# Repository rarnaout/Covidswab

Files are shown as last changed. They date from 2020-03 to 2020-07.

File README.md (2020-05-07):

*Last updated: May 7, 2020*

# Manufacturing NP swabs

Large-scale virological testing for SARS-CoV-2, causative agent of COVID-19, has resulted in an acute shortage in NP swabs across the United States. Ad hoc groups from academia and industry have formed to address this crisis. **This repository organizes output from these efforts**.

The purpose is to **update medical professionals and manufacturers**.

Note the location of the repo has changed.

**Several groups have been testing** various materials and geometries using various protocols. Details:

[Beth Israel Deaconess Medical Center (BIDMC) <i>**Udated May 7**</i>](BIDMC/) | [University of Southern Florida (USF)](USF/) | [University of Washington (UW)](UW/) | [Stanford University](Stanford/) | United States Army

For those with in-house 3D printing capacity who are in the direst need, USF has graciously made an <a href="https://usf.box.com/s/wxmlj0r66vp8bzei6o7sur1kq1jr8o1i">STL file available, along with instructions that you should read first</a>. **However, <u>we strongly caution that NP swabs are a serious undertaking that can carry risk to patients if not carefully evaluated, by professionals, at multiple steps of development and use (e.g. design, materials)</u>, as the groups listed here have been doing. If you can work with a known manufacturer, you are strongly encouraged to do so instead of printing your own swabs.**

**All readers** are reminded that swabs are an FDA Class 1 exempt medical device not suitable for "garage testing." ENT, ER, and ID personnel do not need more work removing foreign bodies from/repairing damage to/treating infections in nasal cavities.

At this point **we discourage randomly printing/testing STL files**; instead please see results from testing sites above (esp. [USF](/USF), if you have your own printing capacity).

The content here is **not medical advice.**

Progress has been possible only because of the **extraordinary openness and sharing** of everyone involved, an inspirational and selfless victory over ego and related temptations.

As we move closer to large-scale manufacturing, contracts, etc. participants are asked to **involve their respective communications offices** before using each others' names in any promotional materials.

We are driven by a **single, common goal: stopping this pandemic.**

Anything is this repo is provided **[freely and openly](Participant_Agreement/)** in the spirit of cooperation for the free use for all.

### Disclaimer

The information and designs in this repository are being made available for research and informational purposes only.  The products described in this repository may be regulated as medical devices depending on their intended use.  The information and designs are made available without any representations or warranties of any kind, including that the designs do not infringe any third-party rights or are appropriate for use in the manufacturing of medical devices.  Any product feedback offered by any medical professional or employee of a hospital provided through this repository does not constitute medical advice or an endorsement of any particular design. Any use of the information or designs in this repository is at the sole risk of the user.

## Contact

BIDMC: Ramy Arnaout, MD, DPhil rarnaout at-sign bidmc dot harvard dot edu 617-538-5681

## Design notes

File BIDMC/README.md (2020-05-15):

*Last modified: Thursday, May 7, 2020*

# Results summary, BIDMC

## Wednesday, May 13, 2020

Our work, detailing NP swab development and clinical validation, has now been peer reviewed and published by the <a href="https://jcm.asm.org/content/early/2020/05/11/JCM.00876-20"> Journal of Clinical Microbiology</a>.

Clinically validated swabs are now available to <a href="https://printedswabs.org/"> order</a>

## Thursday, May 7, 2020

The <a href="https://www.medrxiv.org/content/10.1101/2020.04.14.20065094v2">second version</a> of our preprint is now up on medRxiv, including results from HP, Inc (Abiogenix/Fathom).

## Monday, May 4, 2020

**Regarding viral transport media,** colleagues here at BIDMC have posted a preprint describing the <a href="https://www.medrxiv.org/content/10.1101/2020.04.29.20085514v1">large-scale, in-house production of viral transport media to support SARS-CoV-2 PCR testing in a multi-hospital healthcare network during the COVID-19 pandemic</a>. If you need to produce your own media, please see this manuscript.

## Sunday, April 19, 2020--updated Friday, April 24, 2020

<a href="https://www.medrxiv.org/content/10.1101/2020.04.14.20065094v1">The first results of our field trial are now on medRxiv</a>. (Note apparently medRxiv has been having issues.) In addition to what's in the preprint, a prototype from HP, Inc. has also passed our trial. We will be updating medRxiv as we can.

The participant information sheet we used is <a href="BIDMC_participant_information_sheet.pdf">here</a>. **Remember, approval of such a document requires approval of Your IRB.**

The raw data for Fig. 2 is <a href="fig2_data.txt">here</a>.

Contact information for manufacturers is <a href="https://printedswabs.org">here</a>.

**We continue to make our work freely available to help everyone address the crisis. If you use any of the work here, please do cite the repo and the prprint, Callahan et al. medRxiv 2020.**

## Friday, April 17, 2020

**A brief note: we have received very many requests for our results regarding FormLabs' prototypes. You can find them in <a href="np_swab_results.xlsx">this Excel spreadsheet</a>. None of the prototypes we received from FormLabs passed our Phase I testing. We deemed them too brittle. Therefore none entered our clinical trial. If you have questions about clinical evaluation of FormLabs' swabs, please contact USF/Northwell, as they are the ones with the most experience with these swabs in a clinical context and can advise.**

## Wednesday, April 15, 2020

This entry contains a short summary of progress over the past 10 days at BIDMC, one of the many groups that are working together to resolve the NP swab shortage. It will also try to address frequently-asked questions.

### Contents
- <a href="#field_trial">Field trial results</a>
- <a href="#irb">BIDMC IRB materials for reuse</a>
- <a href="#process_041520">Process update</a>

### Field trial results

About two weeks ago we began an IRB-approved field trial of select prototypes that had passed our initial phases of testing. (Please see prior updates for details of those phases.)

The main goal of the trial was to measure concordance between each prototype and a control, for which we used Copan model 501CS01, one of the FDA's approved standard (flocked) NP swabs. Participants were drawn from the pool of people clinically suspected of COVID-19 who were given appointments at BIDMC's drive-through testing facility.

Specifically, the goal was to collect a prototype as well as a control NP swab on each participant until we had 10 SARS-CoV-2-positive and SARS-CoV-2-negative controls. These were all tested on our in-house Abbott m2000s.

To date prototypes from three manufacturers have completed the trial, with others at various stages. The three are from Resolution Medical (crafted with Carbon3D technology), EnvisionTec, and Origin.io. (Note we have not tested FormLabs.) These all exhibited a high degree of concordance with the controls. Analysis of Ct values showed no statistical evidence of bias, although the numbers are small. Participants tolerated the prototypes to varying degrees.

We have written up the results and posted them to medRxiv so everyone can see details; unfortunately it is taking a bit longer to get a link from them than we wished but we will post it here.

Manufacturers are continuing to iterate on their designs.

The trial is ongoing.

### BIDMC IRB materials for reuse

To help others who want to run a trial, we have made <a href="BIDMC_IRB_key_info.pdf">relevant sections from our IRB available</a>, including <a href="BIDMC_participant_information_sheet.pdf">participant information sheet</a>. If you use them, please cite Callahan et al., medRxiv 2020 (link pending).

### Process update

Manufacturers have launched a <a href="https://printedswabs.org/">site for connecting hospitals with manufacturers</a>. To our knowledge, not all manufacturers appear there. Appearing on that site does not count as an endorsement from BIDMC.

We continue to receive many inquiries. If you are a manufacturer interested in our testing your swabs, the best thing is to send a high-resolution image and, if you can (to cut down on lead time, but unfortunately not as a guarantee we will test), send a complete description (including manufacturer; sender; manufacturing technique; detailed measurements of head, neck, breakpoint, and shaft; production volume now, in one week, and in one month), to CLS624 c/o Cody Callahan, 3 Blackfan Circle, Boston, MA 02215.

Regarding phone and email inquiries: we are happy to help as we can but please do read all the information here and below before sending an email or placing a call, as  your questions may already be answered.

## Friday, April 3, 2020

This entry contains a summary of progress over the past week at BIDMC, one of the many groups that are working together to resolve the NP swab shortage. It will also try to address frequently-asked questions.

### Contents
- <a href="#phase1">Phase I testing: expert evaluation, collection sufficiency, PCR compatibility</a>
- <a href="#phase2">Phase II testing: decontamination, packaging, volume</a>
- <a href="#phase3">Phase III testing: field trial (IRB)</a>
- <a href="#self">Self-printing</a>
- <a href="#process">Process update</a>
- <a href="#next">Next steps</a>

### Phase I testing: expert evaluation, collection sufficiency, PCR compatibility

Earlier this week we completed <a href="../BIDMC/np_swab_results.xlsx">Phase I testing</a> of over 140 materials and prototypes from approximately two dozen manufacturers and other groups.

This phase consists of three steps: (i) expert evaluation, (ii) collection sufficiency (using Gram stain of cheek swab as a proxy for the nasopharynx), (iii) compatibility with our Covid-19 PCR test (we are currently using the Abbott system).

At this point we have completed many (>5-10) iterations of prototypes with several manufacturers, at each step offering design feedback and guidance, working with their engineers, and they have been unbelievably responsive and ingenious in working with us.

### Phase II testing: decontamination, packaging, volume

As we have moved past Phase I, we considered the ability to decontaminate, with a preference for autoclaving; the ability to package singly, and to produce swabs at high volume---hundreds of thousands of units per day or more---and for low cost. This evaluation was done again through many interations with manufacturers.

These two phases resulted in our selection of four prototypes at present---from Carbon3D, EnvisionTEC, Hewlett Packard, and Origin 3D Manufacturing---for Phase III testing, a field trial under IRB (below).

#### How to interpret our selections

We have chosen the prototypes that, per our Phase I and II evaluation above, performed best.

We have chosen prototypes produced via different technologies and materials to maximize our probability of finding solutions and minimize the probability that unforeseen issues results in a future supply bottleneck (such as the one that led to this crisis). We are fortunate that our Covid and respiratory pathogen testing bandwidth at BIDMC allows for testing at scale.

The prototypes we have chosen reflect our best judgment. The Phase I data is collected and freely available to others in this directory. We recognize that others are free to reach their own conclusions and that specific requirements may differ by setting.

#### Additional prototypes

We announced that we would be testing everything received before 5 p.m. Eastern this past Monday, March 2. Mainly for bandwidth reasons we are discouraging new submissions at BIDMC. Other sites may still be accepting. We will try to facilitate connecting manufacturers with additional testing sites if we are asked.

### Phase III testing: field trial (IRB)

As mentioned above, today we began field testing under an IRB. Briefly we are collecting 10 positives and 10 negatives for control swabs and each prototype and testing concordance. We will make details available in this folder as soon as we can. We may add additional prototypes in the future. We will report results in collaboration with the manufacturers.

### Self-printing

We have received many inquiries regarding self-printing. We understand there are sites with on-site 3D printing capacity but effectively no swabs for whom this is a particularly urgent issue. While **we strongly encourage waiting to purchase from a manufacturer if at all possible**, we point those in this urgent situation to the work of Dr. Summer Decker at USF and of FormLabs, who have <a href="https://usf.box.com/s/wxmlj0r66vp8bzei6o7sur1kq1jr8o1i">made available an STL file and a readme</a>. This statement should not be read as an endorsement: the FormLabs solution was not selected for Phase III testing at BIDMC. Our Phase I evaluation of the material for this solution, as for all others we tested, is in the Excel spreadsheet. Again, others are free to reach their own conclusions. **Please read the  disclaimers on this repo's main page, and USF's readme, carefully.**

### Process update

As we move toward what we anticipate will be a successful resolution to this crisis, we understand that competition for credit and contracts will intensify. This is natural. However, **we believe the fastest solution is to remain as collaborative as possible. We encourage manufacturers, and also testing sites, to share as much as they can**. This includes materials testing, protocols, IRBs, and results.

We can give you a folder and write access to post to the repo, for those who want but do not have it. Meanwhile, please make clear what you do not want shared.

### Next steps

We anticipate results of our field trial soon, which we hope to share here and on a 5-minute call.

## Friday, March 27, 2020

This entry contains results of testing over the past two days, as manufacturers have iterated their materials and designs, specifically to **combine** tip and shaft geometries that we preferred with preferred materials.

Please see Wednesday's entry (below) for context.

### Contents
- <a href = "#done">What we have done and not done</a>
- <a href = "#trial">Clinical trial</a>
- <a href = "#decon">Decontamination/sterilization</a>
- <a href = "#package">Packaging</a>
- <a href = "#schedule">Our testing schedule</a>
- <a href = "#guidance">Guidance to other institutions</a>
- <a href = "#notable">Notable performers</a>

### What we have done and not done

In total we have tested <a href="np_swab_results.xlsx">over 100 materials and geometries</a>, contributed by over a dozen groups and individuals.

Prototypes mentioned below pass all three of our initial evaluations: <a href="../BIDMC/Methodology.pdf">design evaluation</a>, <a href="../BIDMC/Methodology.pdf">collection sufficiency</a>, and <a href="../BIDMC/Methodology.pdf">PCR compatibility</a>. **This testing does not constitute a clinical trial.**

### Clinical trial

**None of the prototypes we have received been field tested** yet at BIDMC. An IRB/trial are in preparation (ceding to USF's WIRB). It is not currently our plan at BIDMC to recommend any swab without such trial.

The below does **not** include evaluation of prototypes received after Thursday afternoon; we are working on those now.

**Note for those with in-house 3D printers:** [USF](/USF) has begun field testing of their self-printed swabs.

### Decontamination/sterilization

There is not yet **consensus on sufficient decontamination/sterilization** techniques. Three options are:

- Preferred: autoclaving packaged product
- Backup: ethanol/isopropanol decontamination
- Unknown: vapor-peroxide sterilization

We ask manufacturers of favored designs to tell us what materials are **known to tolerate** these methods, and whether they can be done before delivery.

### Packaging

Single-swab packaging is preferred.

Discussions on these are ongoing. See also note below.

### Our testing schedule

We will continue to evaluate new swabs **received before 5 p.m. ET on Monday, March 30.**

### Guidance to other institutions

**If you can wait** for results of field-testing trials for the above, which gate large-scale production, we recommend you do so.

**If you cannot wait** and have in-house 3D printing capacity, we recommend you [read the University of South Florida's results](/USF), since they have field-tested in-house printed solutions (I believe from FormLabs).

### Notable performers, all-in-one

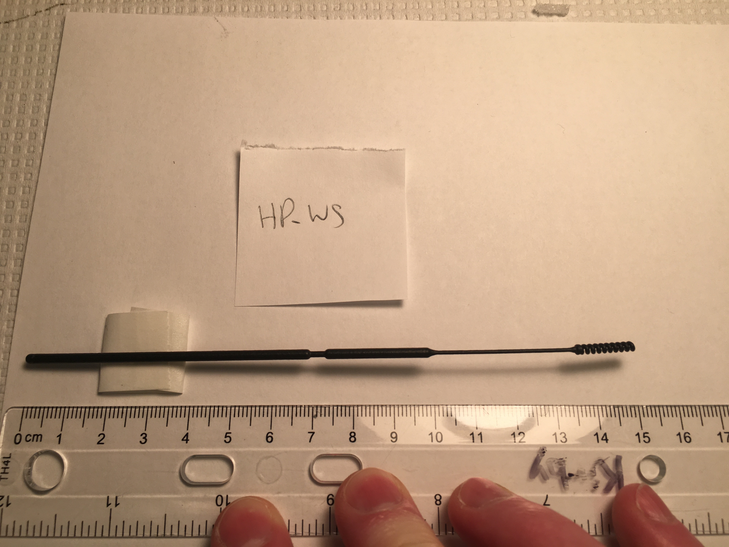
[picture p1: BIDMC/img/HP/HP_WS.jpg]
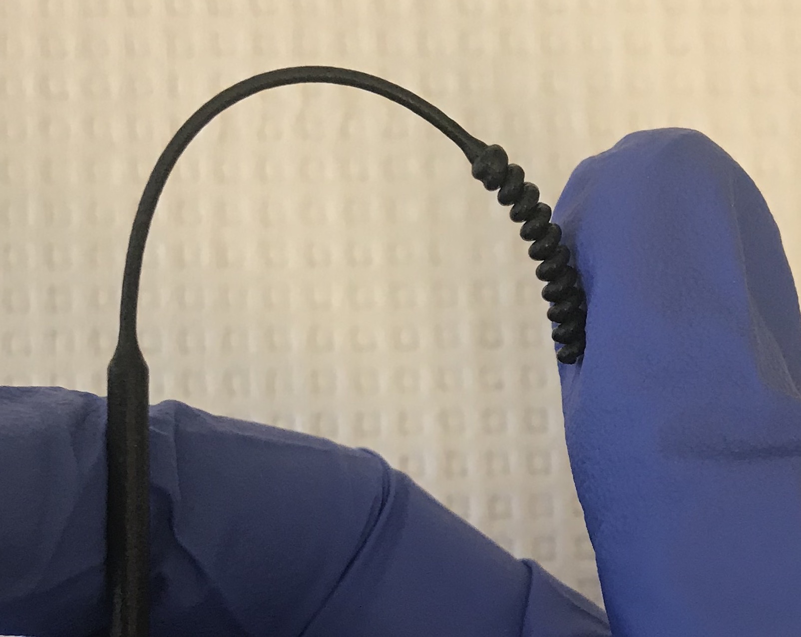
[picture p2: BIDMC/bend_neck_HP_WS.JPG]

HP "WS"

The notability here is the material, which has the same stiffness bendability as the previous version but has a smooth finish. It is autoclavable. The shaft is the preferred design. The breakpoint is a bit difficult to break but acceptable. The tip shown is acceptable but not preferred.

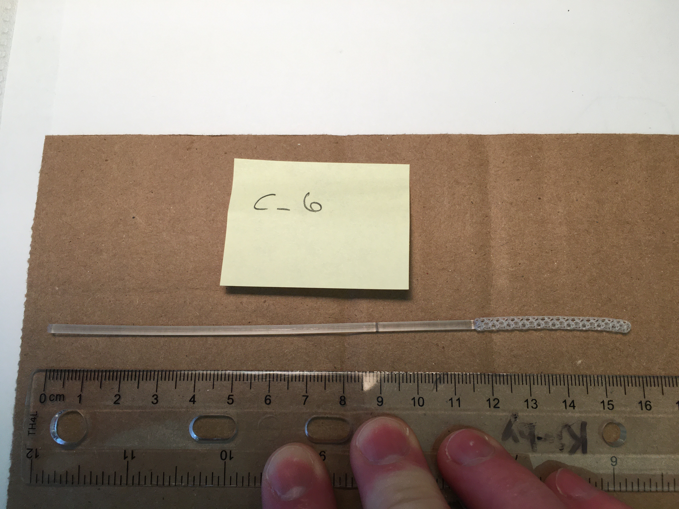
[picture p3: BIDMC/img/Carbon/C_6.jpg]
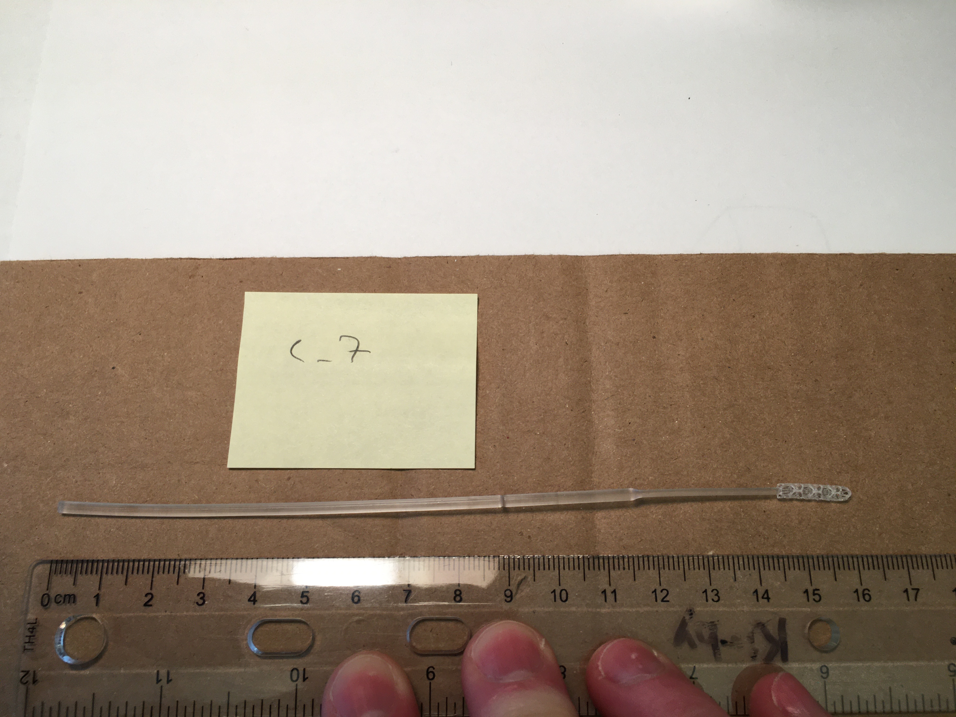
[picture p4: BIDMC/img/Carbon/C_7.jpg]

Carbon "C-6" (left) and Carbon "C-7"

The empty structure collects sufficient specimen. The central spine of the tip provides sufficient rigidity and flexibility. The longer tip provides similar or greater flexibility than the thin neck. The material is not autoclavable but does tolerate alcohol disinfection.

We reiterate that we consider many <a href="#tip">tip designs</a> as passable.

### Contact

Please contact jennifer.kritz@bilh.org for press inquiries.

Please contact Dr. Ramy Arnaout, MD, DPhil rarnaout@bidmc.harvard.edu for technical/clinical issues, and Cody Callahan ccallah4@bidmc.harvard.edu for everything else (including coordinating deliveries/testing).

## Wednesday, March 25, 2020

This document summarizes BIDMC's evaluation of dozens of [**geometries**](#geometries) (swab designs) and [**materials**](#materials) ([full data here](np_swab_results.xlsx)), with brief comments on [**decontamination/sterilization** and **packaging**](#decon), [**production volume**](#volume), and [**clinical trials**](#trials).

- <a href = "#geometries">Geometries</a>
- <a href = "#materials">Materials</a>
- <a href = "#decon">Decontamination/sterilization and packaging</a>
- <a href = "#volume">Production volume</a>
- <a href = "#trials">Clinical trials</a>
- <a href = "#contact">Contact</a>

## Geometries

**Note:** examples shown are not necessarily the preferred material and not necessarily from the manufacturer who created the design. No attribution of credit is made or implied by this listing.

### Tip

Tip should:

- collect sufficient material (see Gram stains below)
- not end in a sharp tip (e.g., spring geometry ends in sharp tip; if tip is connected to support regardless of geometry, result is a sharp tip)
- maximize surface area
- be flexible (more flexible than bic pen)
- restore elastically to straight (even after multiple bending)

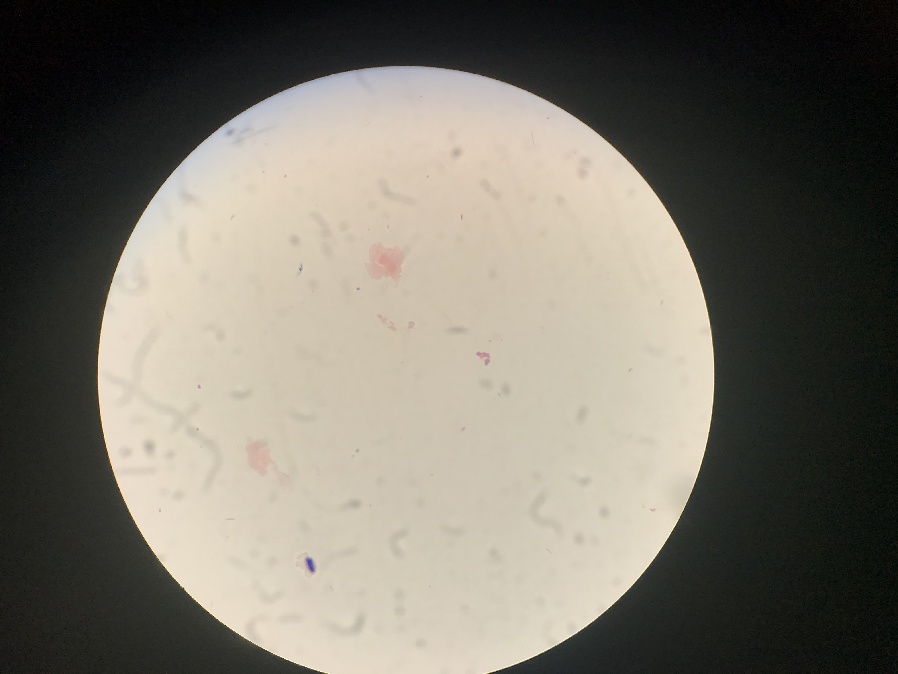
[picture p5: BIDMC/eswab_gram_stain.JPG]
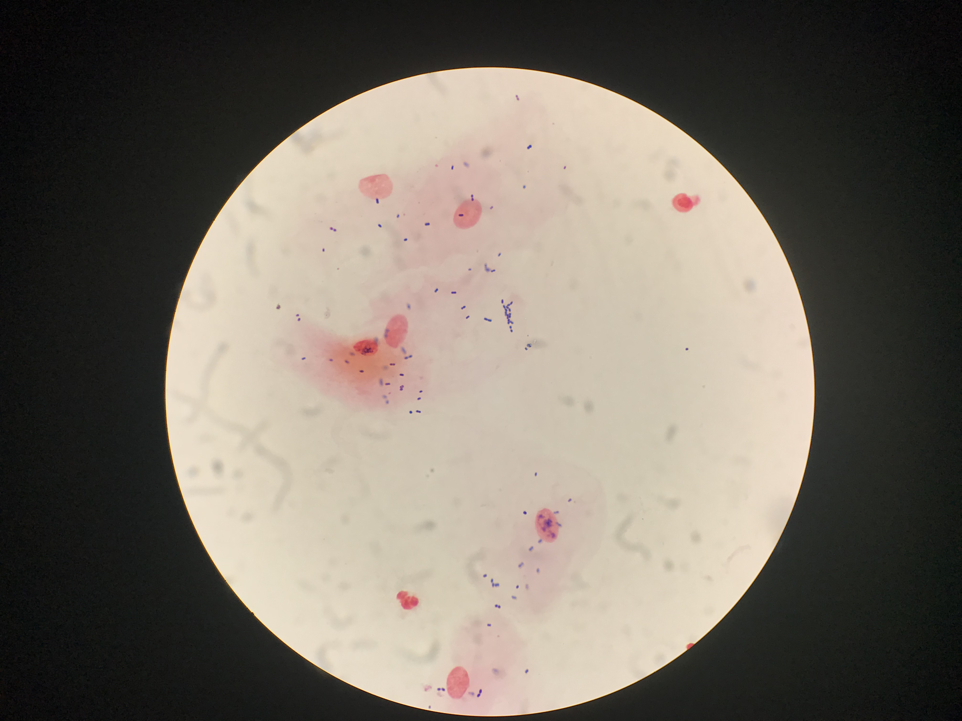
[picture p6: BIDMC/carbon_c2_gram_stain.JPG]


Reference (left) and passing-quality (right) Gram stains of cheek swabs. Epithelial cells (large faint pink) and (Gram-positive) bacteria (small purple) are clearly seen. Many Gram stains of the prototype NP swabs under evaluation (like the one at right) collected more material than the reference (left), but this should not be interpreted quantitatively (a lot/a little), only qualitatively (yes/no).

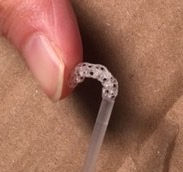
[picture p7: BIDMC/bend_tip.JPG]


Tip flexibility

#### Preferred tip:

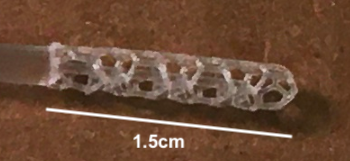
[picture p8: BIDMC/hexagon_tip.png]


Hexagon (Carbon3D)

This was preferred because the hollowness captured a lot of material, while also being reasonably stiff. This was not a strong preference.

#### Also acceptable (no order):

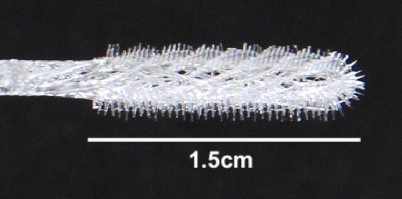
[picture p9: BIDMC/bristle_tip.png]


Bristle (OPT)

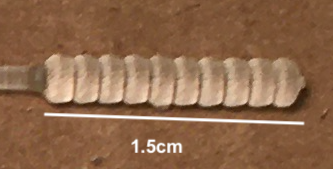
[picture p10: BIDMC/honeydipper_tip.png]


Honeydipper (FormLabs)

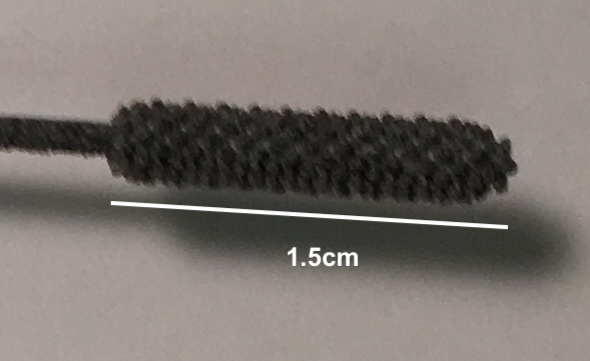
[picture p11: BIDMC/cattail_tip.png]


Cattail (HP print of ?USF design)

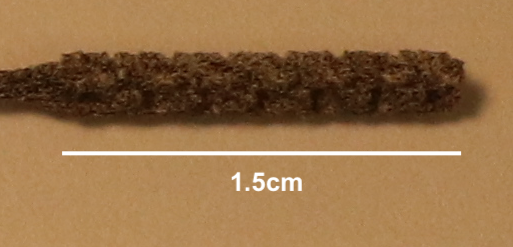
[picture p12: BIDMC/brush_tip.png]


Brush (HP print of ?USF design)

Note none of these are [flocked]("https://github.com/HMS-RIC/Covid19-NP-Swab/#flock"). FDA says flock is **preferred** but **not required**.

### Shaft

#### Preferred shaft:

3mm-diameter tip, 1mm-diameter neck, 2.5mm-dimater handle and \~2mm breakpoint located 7cm from tip-end of swab.

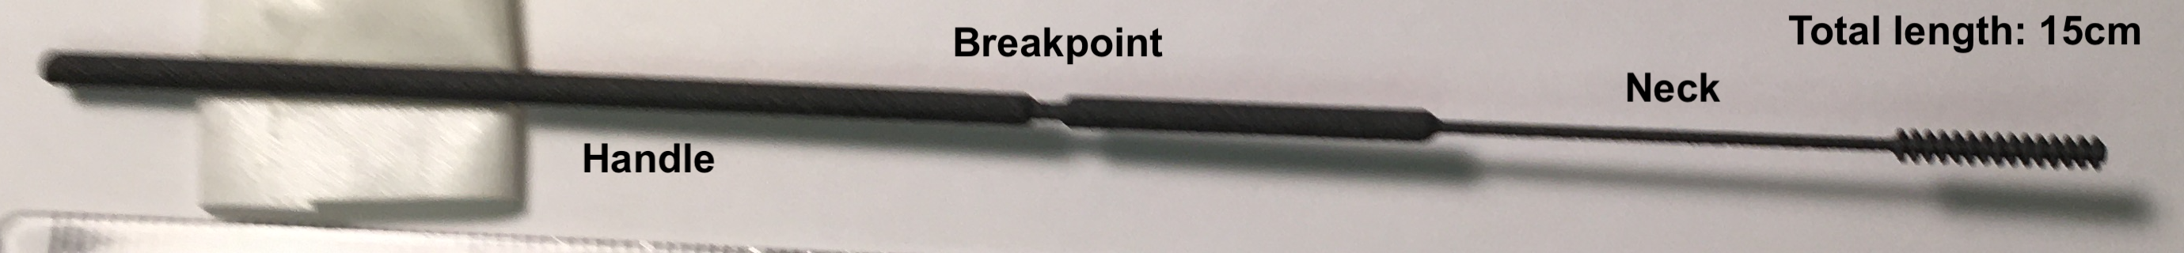
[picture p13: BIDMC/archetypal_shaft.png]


Archetypal (Abiogenix design (?), HP print)

### STL files

We do not have all stl files for all designs tested; what we have are [here](/Covidswab/design_files/). If you need one we don't have, please contact its [creator]("np_swab_results.xlsx"). If you have an stl file to share, please email it to ccallah4@bidmc.harvard.edu with *STL-FILE_\<identifier>_\<company>* in the subject field.

## Materials

### Handling

Key features (best performers in parentheses):

- straight (HP > Carbon3D, FormLabs)
- smooth to the touch (Carbon3D > FormLabs, HP)
- dry (not sticky) (Carbon3D, HP, FormLabs)
- shaft: stiffness comparable to that of the inkholder of a bic pen
- neck and tip: flexible (capable of being bent 180 degrees without breaking, except at the breakopint) (HP, Carbon3D)
- breaks at breakpoint (should be somewhat difficult to do) (HP, FormLabs)
- no dust or other byproduct of printing process

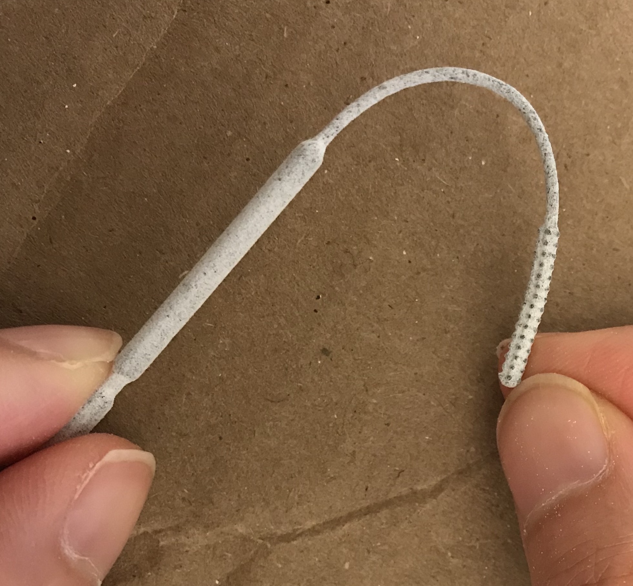
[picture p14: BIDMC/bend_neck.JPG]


Neck flexibility

#### Preferred material:

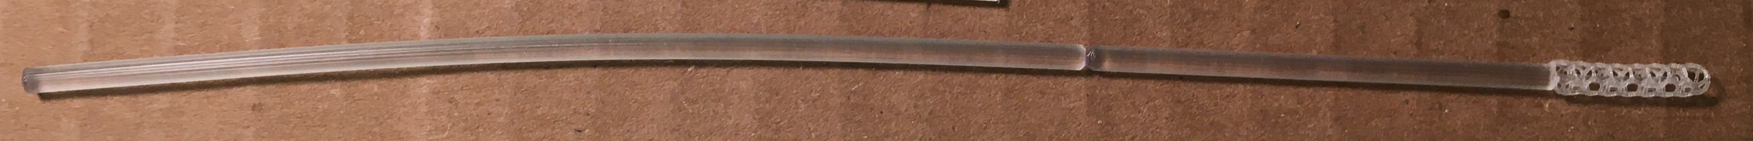
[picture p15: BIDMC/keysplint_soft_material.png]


Keysplint Soft (Carbon3D)

### PCR compatibility

All materials tested so far (as of March 25, 2020) are PCR compatibile (see Excel for any codenames).

**Passed:** OPT, HP ("USF-1"), EnvisionTec (Nilson), FormLabs, Carbon3D, Pavel.

**Pending:** J_1 (Jifei), USF-2, B_1, S_1 (Seriano), EV.

**Not tested (failed clinical testing):** FT

**Not listed here:** materials from compound manufacturing (shaft plus glue plut flock/PDMS)

## Decontamination/sterilization and packaging

Autoclaving preferable, isopropanol or 70% ethanol washes with clean packaging acceptable.

Likely process: swabs produced and washed at scale, then:

- (option 1) take to a company with autoclavable paper packaging (e.g. Georgia-Pacific, 3M), or

- (option 2) packaged at manufacturer's site (e.g. EnvisionTec)

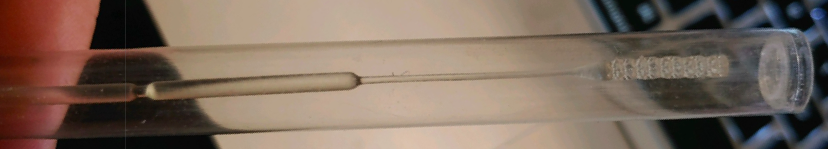
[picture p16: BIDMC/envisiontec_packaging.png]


EnvisionTec's packaging

## Production volume

To my knowledge EnvisionTec, HP, FormLabs, and Carbon3D all have capacity for producing at least hundreds of thousands per day.

## Field testing, safety, market

**Field testing.** Field testing means using swabs on nasopharynx of people with confirmed SARS-CoV-2.

At BIDMC we have tested for appropriateness by (infectious disease/clinical pathologist) expert evaluation, and tested for sufficiency of collection using cheek swab and Gram stain as a surrogate for viral particle collection from nasopharynx. We have **not** field tested.

Field testing requires IRB approval.

To my knowledge Dr. Summer Decker at USF has field-tested at least on non COVID-19-suspected cases. She has an IRB.

I suggest as a first step other clinical sites model after USF's IRB and have their local IRBs cede review to USF as URB of record.

**Safety.** Note swabs are FDA Class-1 exempt devices; "garage testing" not advised.

**Market.** Several tip/shaft/material combinations will likely yield usable products. There will be a competitive market. A/B testing, marketing, contracting, etc. are beyond the scope of this document.

## Injection molding:
For those looking to have injection molded swabs evaluated we encourage you to look through the results of our assessments. <a href="/BIDMC/np_swab_results.xlsx">Here</a>, we offer design feedback and the results of PCR compatibility. In general, effective tip designs have high surface area and are designed not to be abrasive for patients. For material choice, swab rigidness should be comparable to the plastic inkwell of a pen.

In addition, for those looking to reach out, please include information on your ramp up time and daily unit production.

## Contact

Ramy Arnaout, MD, DPhil rarnaout at-sign bidmc dot harvard dot edu 617-538-5681 on behalf of the BIDMC team (not everyone is pictured):

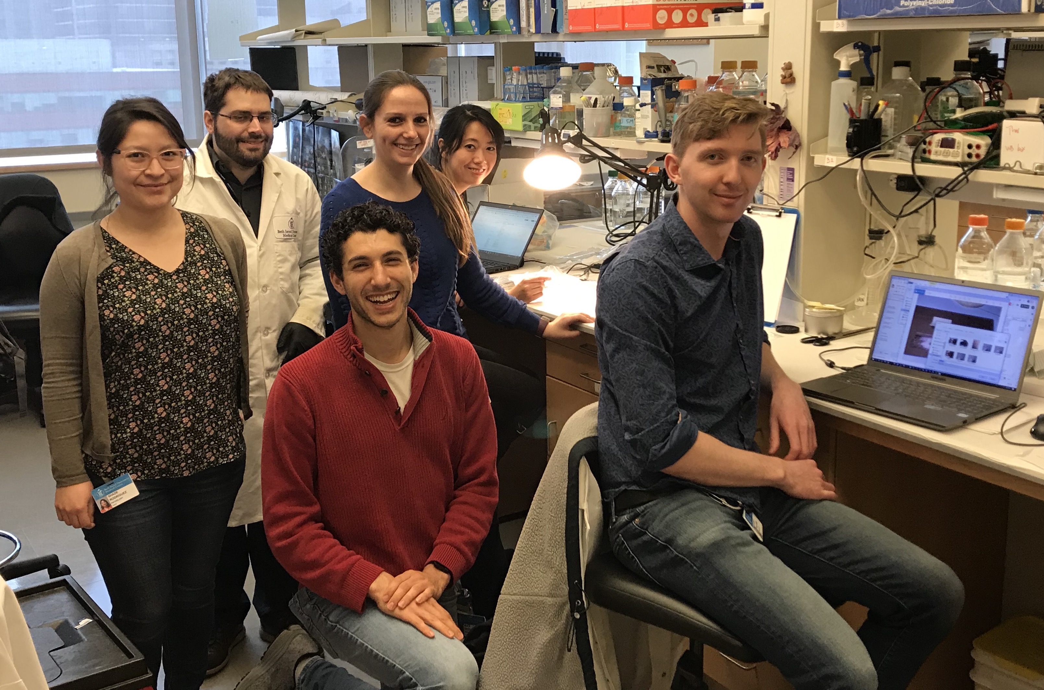
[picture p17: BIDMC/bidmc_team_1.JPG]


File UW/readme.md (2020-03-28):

Notes on work being done in Seattle:

Clinical evaluations were done by Dr. Ellen Lackermann at Pacific Medical Center, she's been working at Pac-Med's drive-through swab clinic.

Sample collection testing was done by Jenny Hu, stains were done on slides with methylene blue instead of gram stain.

PCR compatibility testing done at UW Department of Laboratory Medicine, Virology Division by Keith Jerome's group (using Covid-19 sample)

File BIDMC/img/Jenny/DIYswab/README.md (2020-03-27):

*Last updated: March 23, 2020 00:15 PT*

# VWR 1ul inoculating loop with a strip of Pellon P45 fabrif double knotted through the loop.  

Use a dental floss threader to pull the fabric through loop.  Need to hold the loop while pulling through so it doesn't bend/snap.

video of process here: https://www.dropbox.com/s/hvpb7n1sn2xzr8p/loop%2Bpellon%20p45.mp4?dl=0

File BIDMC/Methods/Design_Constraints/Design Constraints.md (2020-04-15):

# Mechanical Constraints
Swab
- outer diameter of swab is 3mm or less
- minimum swab length is 15cm - *confirm this*
- swab should flex (75 degrees with ?lb load) - *confirm this*
- swab should break 7cm from tip

Swab Bristles
- should be 1.5cm in length
- bristles should maximize surface area
- bristles should not dislodge/break off in body
- bristle head should not break off in body

Swab Break
- part should break first at swab break

# 3D Printing Constraints
Resolution
- minimum feature size/resolution of MJF 3D printing is 0.7mm
Material
- material is PA11 or PA12 nylon - confirmed FDA biocompatible 

# Material Constraints
PCR/Assay Compatability

## Safe: 

- PC, 
- PVC, 
- PP, 
- PTFE, 
- wax with melting point ≥80°C, 
- SiO2 quartz, 
- Pyrex glass, 
- soda-lime glass, 
- NOA68, 
- mineral oil

## Unsafe: 

- PMMA, (incompatible with PCR)
- wax with melting point <80°C, (incompatible with PCR)
- silicon, (incompatible with PCR)
- SO2 5600Å, (incompatible with PCR)
- ITP glass, (incompatible with PCR)
- SU-8, (incompatible with PCR)
- NOA61, (incompatible with PCR)
- epoly glue, (incompatible with PCR)
- acrylic glue (incompatible with PCR)

## Source:

Kodzius et al [paper](kodzius2012.pdf): Inhibitory effect of common microfluidic materials on PCR outcome

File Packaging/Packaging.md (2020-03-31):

# Packaging Prototype Overview

The following is a brief overview of the different packaging methodologies submitted for evaluation. Here, we describe the advantages of each system, as conveyed to us the respective manufacturer and or designer.
<br>
<br>
<br>

## EnvisionTec
<p>
EnvisionTec has an FDA approved single-swab packaging system, that is capable of printing both the swab and container simultaneously.
</p>
<br>

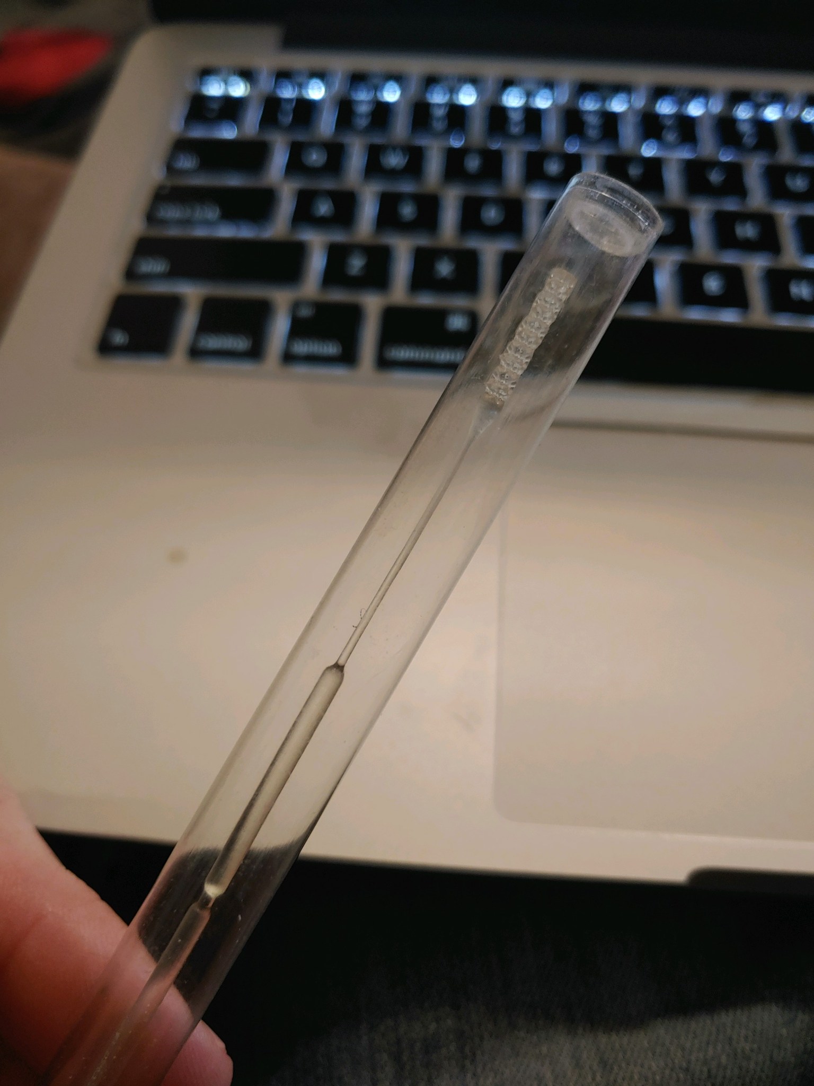
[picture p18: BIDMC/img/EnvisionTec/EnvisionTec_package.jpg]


<br>
<br>
<br>

## Opt Industries
<p>
Opt Industries has provided designs for a multi-swab system to maximize the amount of swabs available per print. In this design, multiple swabs are printed per case, with individual swabs being pulled out of the case as needed.
</p>



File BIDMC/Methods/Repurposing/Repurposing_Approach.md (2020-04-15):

*Last updated: March 20, 2020; info-dumped, needs better organization*

### Scrounging, Repurposing

First a word about scrounging and repurposing. There are lots of swabs used for various things floating around hospitals, outpatient clinics, private practices, and so on. **Be creative and ask everyone you know. That's what we've been doing and it's gotten us thousands of swabs.** This is a stopgap at best, but every swab counts.

Will a repurposed swab work? Find someone who uses NP swabs, take pictures of what you find, and ask that person to weigh in on suitability. (We've been asking our respiratory care personnel.) In practice, as long as the materials are not wood or cotton, there's a chance you've got something usable. **If you find something that works, please tell us,** along with how you know it works, and we'll post it.

There are several alternatives being tried:

- We are looking into using small urine loops as shafts; we don't yet have a solution for how to apply a swab end. Will post if we do. At least there are usually very many of these around in clinical microbiology laboratories
- Printing a bristled head is a no-go for conventional 3D printers, as the features are too small. It is possible that a sand-blasted/chemically etched/otherwise roughened bulb *might* work, but we are not doing research here: we're looking for our best bet for a sure thing
- Mascara brushes. The consensus so far is, the materials might be right but the brushes are far too large/widely spaced. Again, they *might* work, but see above

SWAB-LIKE PRODUCTS
----------------------------------
1) optics (cleaning supplies)
2) cosmetic swabs / applicators
<!-- 3) all the research Ofer and Pavel have done -->

SHAFTS
------------
1) loops (see picture)
2) plastic rod
   1) 2mm nylon fishing line
       comes on a roll but may be stiff enough
   2) plastic rod
3) thin pipettes (Rima)



BRISTLE W/O ADHESIVES
--------------------------------------
1) knurling process to crush plastic to give it a high-surface area feature (can be done with a vice and rough surface plates;  burnish sharp edges)
2) sanding / sand blasting to roughen edges
3) chemical etching to roughen edges
4) reheating plastic locally and forcing into a mold (need to watch out for brittleness)
5) molding/3D printing shape

BRISTLE W/ ADHESIVES
-----------------------------------
1) flocking
2) absorptive foam  (open-cell, like paint-brush)
3) tooth-brush material
4) nylon wool fiber (https://www.polysciences.com/skin/frontend/default/polysciences/pdf/Nylon%20Wool.pdf)
5) panty-hose material (nylon mesh; can be cut and wrapped/wound)
6) synthetic steel wool (https://www.amazon.com/3M-10119NA-Synthetic-Steel-Wool/dp/B00004Z4AE)

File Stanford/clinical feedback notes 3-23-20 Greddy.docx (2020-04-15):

Clinical Feedback meeting notes by Goutam Reddy (greddy@abiogenix.com)

3/23/20 meeting @ Stanford Health

Interviewed: Dr. Linda Barman, Thanh Khong PAC (they run the drive-through swabbings)

Summary of Design Notes:

1) Features too sharp => need a smoother edge (like flocking) - suggested a “rounded Archimedes screw”
2) Need a rounder tip (like bulb of flocked head) w/ “cupping”
3) Need to stiffen break-point and move back
4) Need plastic to bend but not deform => spring back after bending (liked thicker diameter neck models than thinner)
5) Most liked designs #3, #10, #1
6) Finer features not showing up in PA12 prints (PA11 vs PA12?)

Swab Note:

They use a swab with a longer cut-off point. She said our cut-off point was too short (nasal swab vs. nasopharyngeal swab?) Measurements of the swabs they use below:

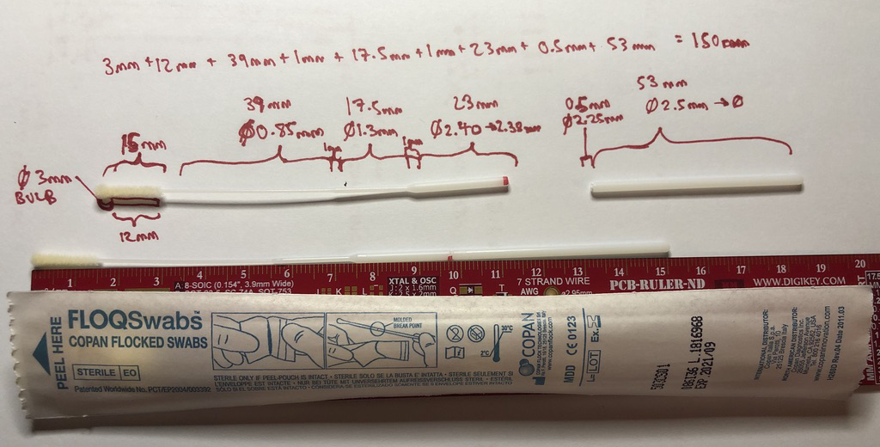
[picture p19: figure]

General Notes:

1) We should test temperature changes of our swabs as they can be sitting in freezing temperatures for drive-through clinics.
2) Asked about sterilization and packaging -> is it autoclavable?
3) Nasopharyngeal space is extremely sensitive (to bleeding, irritation etc…), especially in patients coming in to be swabbed. Err on the side of doing no harm (i.e. swabbing is not a life-saving intervention => we’ll be doing millions of swabs => err on side of gentle np swab and no damage to tissues (no poking, soft interface, no breaking off inside so ENT has to extract)

Test 1) Abiogenix Nubs w/ Holes in PA11 (mfg by HP in San Diego)

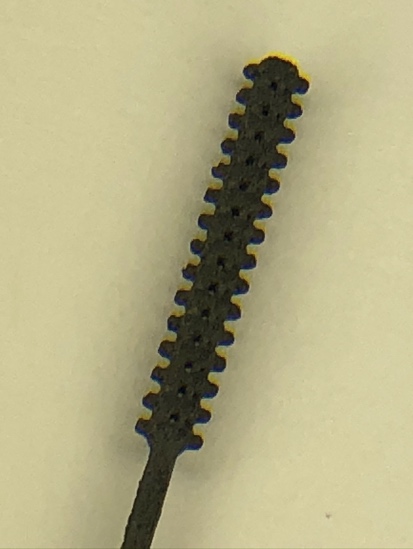
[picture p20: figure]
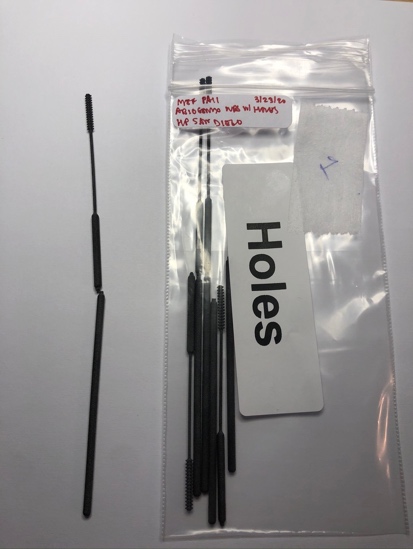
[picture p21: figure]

- too flimsy @ breakoff point => stiffen @ breakoff
- breakpoint too far down
- too rough

Test 2) Abiogenix Nubs w/o Holes in PA11 (mfg by HP in San Diego)

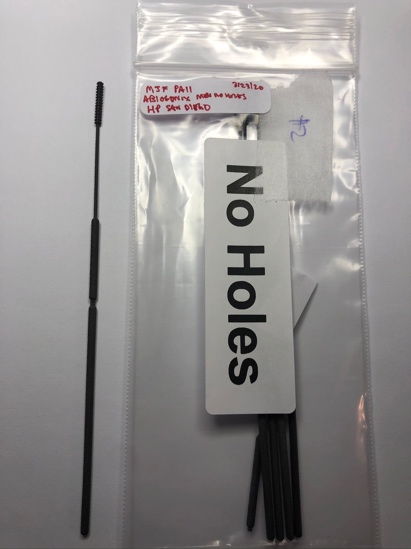
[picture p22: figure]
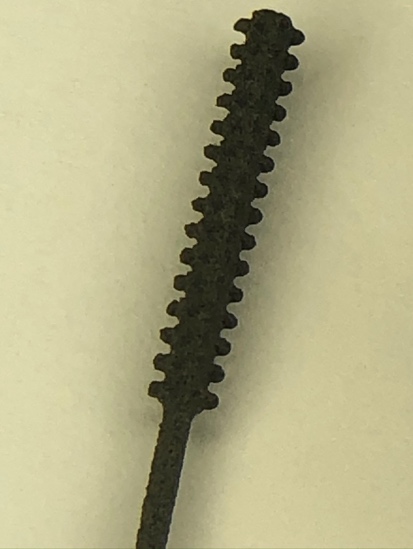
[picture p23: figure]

- needs rounded tip like the bulb on the flocked swab
- tip is too tiny: needs absorption
- passage to nasopharynx has bends, so swab needs to bend but needs to spring back

Test 3) Fathom ??? in PA12 (mfg by Fathom in Oakland)

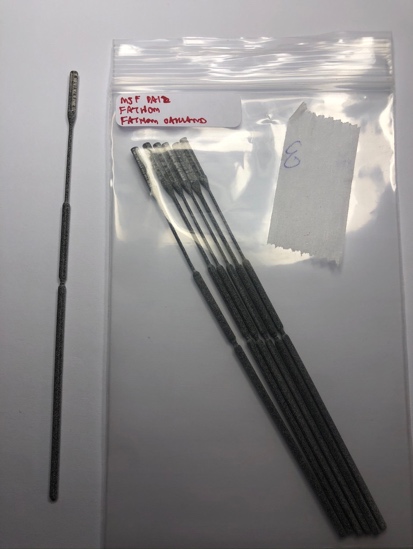
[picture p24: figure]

- liked round tip
- smooth out
- make neck longer
- good size
- good front
- good neck

Test 4) Fathom ??? in PA12 (mfg by Fathom in Oakland)


- too brittle
- ripped off tip
- too small
- too thin
- not sure which one this was – check inventory of prints from 3/23/20

Test 5) Fathom ??? in PA12 (mfg by Fathom in Oakland)


- heads breaking off
- “medieval torture device”
- shaft too brittle

Test 6) Abiogenix Nubs in PA12 (mfg by Fathom in Oakland)


- “weapon”
- shaft breaking
- in general: needs rebound: needs higher elasticity

Test 7 & 8) Abiogenix Round Tip in PA12 (mfg by Fathom in Oakland)


- no notes

Test 9) Fathom ??? in PA12 (mfg by Fathom in Oakland)


- Tip ripped off
- Too small
- Too thin

Test 10) Wyss Balls in PA12 (mfg by Fathom in Oakland)


- “head too wide”
- like roundness
- suggested archimedes screw => rounded w/ cupping and capture fluid, like a “staircase with smooth edges”

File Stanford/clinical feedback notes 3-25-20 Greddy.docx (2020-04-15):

Clinical Feedback meeting notes by Goutam Reddy (greddy@abiogenix.com)

3/25/20 meeting @ Stanford Health

Interviewed: Dr. Linda Barman, Thanh Khong PAC (they run the drive-through swabbings)

Summary of Design Notes:

1) Most liked designs #15 > #13 > #11
2) Liked rounded tips
3) Liked wider necks
4) Liked USF design because it had a 100mm break-point with longer neck
5) Materials Comparison:

They liked PA11 the best because of the springback of the neck.

PA12G (gray) was too stiff and PA12W (white) was too weak.

Requested feel of a slightly stiffer PA11.

6) Want more elasticity from designs (spring-back). The nasopharynx has a kink ( "a little hill" and go down; want overall trajectory to be straight but go over the hill)

Swab Note:

The swab Stanford Health is using is Copan 503CS01, which has a 100mm breakpoint.

They both said our cut-off point was too short (again). See previous note for full measurements.

General Notes:

1) We should autoclave our swabs first to test material change prior to testing, and test at different temperatures.
2) For sterility, they suggested EtO as more commonly available than autoclave (globally).
3) d
4) Dr. Barman suggested making a spiral structure in neck to strengthen it
5) There are two techniques for swabbing:
  a. one is “twirling” - rotating the swab in the fingertips 5 times after insertion for 10 seconds
  b. the other is “swirling” (moving the hand with a circular motion)

Suggest we include training materials if there is a preferred way to use this swab.

6) drive-through patients: prefer to have patients look ahead or slightly turned so they can use the headrest for patient to push back against when expecting recoil of head from insertion of np swab

Test 11) Wyss Spiral in PA12 (mfg by Fathom in Oakland)


- like it; not bad; - as long as it doesn't break - too flexible: may jam in their nose - too brittle - you’re gonna get jammed up; make it less brittle and stiffer - breaks too easily | | | are you gonna get locked up; make it less brittle and stiffer | | | breaks too easily

Test 12) USF PA12 (mfg by HP in San Diego)


- liked burr tip
- note burrs do not come out in prints
- neck flexed and broke
- like that the breakpoint is moved up
- feels more like it won’t break in my hand
- feels harsh, too brittle, but like length
- check at different temperatures
- NOTE: burrs are inconsistent (too small features) for current MJF tech;
- worry burrs may fall/rub off in nasopharynx

Test 13) Fathom Squares Large (mfg by Fathom in Oakland)


- really like rounded tips
- doesn’t feel bad; spring is good
- make neck longer (worried neck is thick too soon; that part goes in nares (neck) ; worried it won't go as deep; narrower and longer neck; like crevices
- check on structural integrity

Test 14) Fathom Squares Tiny (mfg by Fathom in Oakland)


- check with fluid collection
- like roundness and roughness (not too rough)
- NOTE: features did not come out that well in this model

Test 15) Fathom-Barman Screw (mfg by Fathom in Oakland)


- do a torsional test
- great that it’s a little wider [than below designs]
- “my favorite”, “top choice”
- nice rounded top

Test 16, 17, 18, 19) HP Screw and Spring Designs White (mfg by HP Vancouver)


- too flexible
- won't be able to go through
- too pointy at end ; too pokey
- neck too brittle/ fragile => make thicker
- may not be wide enough
- too wimpy ; really breakables;
- not hard enough to guide
- head too small
- really didn’t like PA12W materials

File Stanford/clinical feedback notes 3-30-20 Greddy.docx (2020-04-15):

Clinical Feedback meeting notes by Goutam Reddy (greddy@abiogenix.com)

3/30/20 meeting @ Stanford Health (they run the drive-through swabbings)

Interviewed: Dr. Linda Barman, Thanh Khong PAC, Another Physician

Summary of Design Notes:

1) felt no difference between Frozen vs. Room Temperature swabs
2) Liked spiral design with recommended modifications from other designs:
  a. spiral head w/ rounded tip (Barman design)
  b. move neck-body interface down (to position of spring designs)
  c. thicken breakpoint (okay to bend and twist to break off into tube)
  d. move breakpoint down to 100mm
  e. head of tip is fine, could be a little rounder
  f. tip flimsiness: make sure doesn’t break when bent backwards (pushed against obstruction)

Swab Note:

They liked the 100mm break-off. Once again WARNED that the 80mm break-off would be going into the nose of the patient, or would not reach nasopharynx. <see video>


General Notes:

1) They liked the tube testing: said to test with more kinks/bumps to ensure simulation of blockages and constrictions.
2) They tested by pushing the swab into the palm and backside of their hands to test flexibility
3) They made a constriction of a hole in their hand and tried pushing into the constriction
4) They clenched a fist and twisted in their hand
5) They also twisted and pulled and bent swab to test material strength
6) All colleagues suggested a slight curve to the neck

Test 21) HP Spring 80mm (mfg by HP in San Diego)

- autoclaved at 121 vs 134: no difference
- frozen vs room temperature: no difference


- Like head; end should be rounder (tip rounder)
- snapped neck and snapped head (too brittle, “more brittle”)
- make it stiff, but not brittle
- “will jam up” inside nose
- “too soft, jam up and not go”
- Spring is too floppy, “too floppy”
- Stiffen shaft a little
- Spring harder to get through

Test 22) HP Spring 100mm (mfg by HP in San Diego)

- autoclaved at 121 vs 134: no difference
- frozen vs room temperature: no difference


- spring way too wiggly; like spiral because it is stiffer
- spring too bendy
- neck too skinny -> make thicker
- want a little stiffer than spring, but not breakable like spiral
- like breakpoint placement

Test 23) Fathom Squares in PA12 (mfg by HP in San Diego)


- not rounded enough
- stiffer than spring
- like thickness of neck
- make the breakpoints (for all) harder to break;
  - if you have to bend and twist, its no problem
- the cutdown is too thin

Test 24) Barman-Fathom Spiral in PA12 (mfg by HP in San Diego)


- like this head the best (not as stiff as squares, not as flimsy as springs)
- tip okay, but round out tip even more if you can
- neck not long enough = make longer
- broke neck by flexing
- breakpoint is too deep of a cut => make stronger
  - don’t’ want to snap off inside someone’s nose
- move breakpoint to 100mm design

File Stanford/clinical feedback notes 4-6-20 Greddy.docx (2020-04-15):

Clinical Feedback meeting notes by Goutam Reddy (greddy@abiogenix.com)

4/6/20 meeting @ Stanford Health (they run the drive-through swabbings)

Interviewed: Dr. Linda Barman, Thanh Khong PAC, Multiple other Stanford Physicians

Summary of Design Notes:

1) Really like black material
  a. it’s a little more springy
  b. feels better (smoother)
  c. is more flexible
2) Recommendations:
  a. liked pre-flex, said could be a “little less”
  b. thicken breakpoint (okay to bend and twist to break off into tube)
  c. move breakpoint down to 100mm
  d. move neck-body interface down (by 2cm)
  e. liked roundness of head
  f. wondered whether spring head will pick up enough material
  g. want to test against spiral

Swab Note:

Again- wanted 100mm break-point with neck moved down by 2cm.

General Notes:

1) Asked about catching: yes, catching and bending on an obstruction happens
2) New people will push up instead of down and will kink the head sometimes
3) Tested for max-torque (torque wrench + socket bit + thermosteel + dremel chuck)
  a. max torque is definitely below 5lbf-in (minimum of test tool)
  b. estimated to be below 3lbf-in.


Test 25) HP Spring Black Vapor 80mm (mfg by HP in San Diego)

- autoclaved at 121 at LLNL


- breakpoint: make much harder to break still
- breakpoint: give it a chunkier waist
- breakpoint: minimal scoring -> much shorter cut
- breakpoint: only thin it out a little more
- a tiny less curvature to bend
- is tip “too smooth”? will it pick up material
- will the spring collect enough material
- can make a hole in middle of it (discussed previous design that had hole, but was too sharp)
- like black material: more springy, more flexible, better feel, like springiness


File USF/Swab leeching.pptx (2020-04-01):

## Swab leeching

1. 2 ml of BD UTM was spiked or not with 10⁶ PFU of RSV and aliquoted to 2 1.8 ml cryotubes.
2. One sterile swab tip was cut off into one tube.
3. Cryotubes were incubated at 4oC, 24 hr.
4. 140 µl UTM from each tube was subjected to RNA isolation with Qiagen viral RNA mini kit, elution in 50 µl.
5. 10 ul of RNA was used to make cDNA (iScript, BioRad) in a 20 µl final volume.
6. qRT-PCR was performed with 2 sets of RSV primers for the N gene and the SH-G intergenic region. 2 µl of cDNA per well, triplicate wells. 20 µl qRT-PCR using SensiFAST SYBRgreen kit (Bioline).
7. Shown are cycle thresholds (C(t)), where RSV RNA was detected.

N works better with swab?

C(t)

## Swab leeching

- Same experimental protocol as before, except using WHO VTM made in-house.
- Testing 70% EtOH rinse versus autoclaving as sterilization method.
- Triplicate swabs incubated in WHO VTM at 4oC for 1, 2, and 3 days.

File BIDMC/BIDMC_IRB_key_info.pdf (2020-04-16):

Ramy Arnaout rarnaout@bidmc.harvard.edu BIDMC If you use any of the below, please do cite Callahan et al. medRxiv 2020

PURPOSE OF PROTOCOL

The SARS-CoV-2 pandemic has resulted in an international shortage of the nasopharyngeal (NP) swabs used to collect sample for virological testing. This shortage has become a crisis as testing capacity is growing, and threatens to become the bottleneck at Beth Israel Lahey Health as it already is in other testing centers. To resolve this crisis, a team in the Clinical Microbiology Laboratories at Beth Israel Deaconess Medical Center has been working closely with highvolume domestic manufacturers developing 3D printed NP swabs in an open process involving the hard work of many partners from across the country. This process has resulted in promising prototypes.

We will test these prototypes for non-inferiority relative to existing, already validated NP swabs produced by Copan and/or Puritan (“control swab”) for purposes of molecular microbiology: i.e., the PCR tests used for virological testing for SARS-CoV-2 and for multiplex testing using Genmark’s ePlex respiratory pathogen panel (RPP). Specifically, we will swab the nasopharynx of patients under investigation (PUI) for Covid-19, the disease caused by SARS-CoV-2, using a prototype, swab using a control swab, and test for concordance of SARS-CoV-2 and RPP results. In all cases we will transport the swab in validated viral transport medium (VTM) as per standard operating procedure at BIDMC.

Primary Objective: To determine whether four newly designed and manufactured NP swabs (“prototype swabs”) perform acceptably compared to standard swabs (“control swabs”) used for collection of nasopharyngeal samples for molecular microbiology, specifically Covid-19 and respiratory pathogen testing by PCR.

SIGNIFICANCE AND BACKGROUND FOR THE STUDY

The SARS-CoV-2 coronavirus is the cause of the Covid-19 pandemic. This novel coronavirus infection was first described in 2019 in China and testing in the United States first became available in early 2020. A linchpin of fighting the pandemic is diagnostic testing for the virus that causes Covid-19. Unfortunately, NP swabs are in limited supply due to the explosive spread of the virus, including in Italy, home to Copan, a leading manufacturer of NP swabs. Control swabs consist of a plastic shaft with a thin neck and a head (or tip) coated with flock, a filamentous material most often made of rayon, nylon, or Dacron. The swab is inserted into the nasopharynx, swirled around, removed, and the tip broken off into a vial containing VTM. The vial is sealed and sent for testing, for which an aliquot of VTM is taken and used as per testing protocol.

BIDMC has been interacting with manufacturers and testing prototypes according to a threestep protocol: (1) expert evaluation by representatives from clinical pathology, infectious disease, and respiratory therapy for features such as stiffness; pliancy of the head, neck, and shaft; and smoothness of material; (2) sufficiency of collection using microscopic evaluation of Gram stain of the cheek vs. control swabs (as a minimally-invasive proxy for NP swabbing); and
(3) PCR compatibility by incubating the swab tip in VTM overnight to soak up or leech out any potential PCR inhibitory substances, spiking with inactivated SARS-CoV-2 viral particles, running our standard test, and confirming positivity.

In addition, working with manufacturers, BIDMC assessed the ability of prototypes to be autoclaved for sterilization, individually packaged, and produced at a rate of hundreds of thousands per day in short order, which are requirements for addressing the pandemic at scale.

Prototypes that passed these tests and assessments were prioritized for the current study.

DESCRIPTION OF RESEARCH PROTOCOL

Study Design – Overview, Methods, Procedures

The study design is a clinical trial to determine whether newly designed and manufactured NP swabs (“prototype swabs”) perform acceptably compared to standard swabs (“control swabs”) used for collection of nasopharyngeal samples for molecular microbiology, specifically Covid-19 and respiratory pathogen testing by PCR.

The study population will consist of approximately 400 emergency-department, inpatient, and “drive-thru” patients seeking evaluation of respiratory complaints in the context of the Covid-19 pandemic.

The study endpoint is confirmation or rejection of concordance between each of the four prototypes vs. control swab. This will be achieved through a test of concordance for 10 positive Covid-19 tests, 10 positive RPP tests (any pathogen), and 10 negatives. Because the study is for Covid-19-positive vs. negative and simultaneously RPP positive vs. negative, the total number of tested swabs may be fewer than 30 (but no fewer than 20) per prototype. Note that to economize testing, there may be collection without testing for some swabs (e.g. if 10 negatives are already collected). No patient will be swabbed with more than a single prototype swab.

Study Intervention/Investigational Agent: The agents consist of four prototypes designed and assessed as described in the “Background” section. Like control swabs, these are 15-16cm in length, with 1-3cm radially symmetric heads of diameter 2-3mm, a thin neck of 4-7cm (diameter 1-2mm), and a thicker shaft (diameter 2-4mm), with a break point most often 7-8cm from the tip of the head to facilitate transport. The materials are various FDA-grade plastics and resins.

Consent: Potential participants at the point of testing, whether drive-thru, ER, or inpatient, will be asked if they are willing to have an additional experimental swab test performed by the treating clinician. The participant will be given a written research information sheet (by study staff) that will include contact information for the study doctor if the participant has any questions. For distribution of participant information sheets and instructions to staff, we will be coordinating with the head of respiratory therapy, Joe Previtera, who is a co-investigator on this study.

Research Procedures: Participants who have been swabbed using control swab as part of standard (i.e., non-study/non-experimental) clinical evaluation will be swabbed with a single prototype as experimental. Prototype swab will be placed in a separate vial of the same BIDMCvalidated VTM solution and sent to the clinical labs for testing.

For each prototype, prototype swabs will be tested until either 10 Covid-19 positives, 10 RPP positives, or 10 negatives are collected, whichever comes first. Thereafter, prototype swabs may be held and tested following result of the accompanying control swab, to bring totals to 10. (This is to avoid unnecessary testing of e.g. extra negatives if 10 negatives have already been obtained.)

Results from control and prototype swabs will be compared for concordance. This is a research study. The result of the prototype swab will not be returned to the patient or entered into the patient record and will not be used for clinical decision-making. This is for research use only. If the research swab result is discordant with the standard of care swab, the study team will notify Chris Rowley or contact the highly infectious disease pager to relay the result. Chris Rowley or the physician carrying the highly infectious disease pager will determine next steps.

Regarding management of discordant results: if results are discordant, the discordant result will simply be recorded as such. Swabbing will not be repeated by the research team.

Data and Specimen Banking: Specimens will be labeled with a subject-specific unique identifier without PHI with the format <PROTOTYPE)_0001.

Specimens will be linked to electronic medical record number (MRN), date specimen was taken, and result of Covid-19 and RPP testing. Specimens and data will be analyzed with subject unique identifier labels without any PHI.

De-identified data will be shared with the sponsor for analysis. Data will be transferred using Excel spreadsheets.

Study Timeline: The study involves a one-time collection of a prototype swab from a patient. For an individual participant, the length of participation in the study will be just enough time for sample collection (approximately 1 minute). The study will run for approximately two weeks, followed by one week of analysis. The length of time to complete the study will depend on manufacturers’ delivery of swabs and the rates of positive and negative results (currently ~15% for Covid-19 on a volume of ~1,000 tests/day). The anticipated total duration of the study is three weeks.

Statistical Considerations | Sample Size Justification: Approximately 400 participants will be
enrolled in the study at BIDMC and will have a prototype swab collected.

For each of the four prototype swabs, we will test 10 positive Covid-19 cases, 10 positive RPP cases, and 10 negatives, for a total of 30 tested prototypes. Thus, given prototypes from four manufacturers, we expect approximately 120 prototype swabs to be tested.In clinical microbiology, it is standard practice to take this approach of identifying 10 positives and negatives to evaluate new swabs (Miller et al. Changing Swabs: To Validate or Not To Validate? J Clin Micro 2013 10.1128/JCM.02023-13).

Data Analysis: Inferential statistics will be done to analyze the extent of agreement of the test results from the two viral collection kits. Quality control checks will be run on the data to detect data that is missing, out of expected ranges, or otherwise questionable.

Data will be recorded using the data collection forms. The data to be collected include (1) demographic data: age, gender, MRN (information available through the electronic health record); (2) date of enrollment; (3) date of specimen collection; (4) Covid-19 positive/negative, using the control swab; (5) RPP pathogen positive/negative, using the control swab; (6) Covid-19 positive/negative, using the prototype swab; (5) RPP pathogen positive/negative, using the prototype swab.

Statistical plan: We will evaluate using Cohen’s kappa, the normed difference between the rate of agreement that is actually observed and the rate of agreement that would be expected purely by chance (Kwiecien et al. Dtsch Arztebl Int. 2011 Jul; 108(30): 515–521).

Study data may be stored for up to 6 years.

Subject Selection | Inclusion Criteria: Individuals presenting to the site for clinical care will be
evaluated for clinical screening for Covid-19 testing or other respiratory infection testing. Individuals felt identified clinically as needing Covid-19 testing may be approached for study participation. If the patient provides verbal informed consent, specimen collection with the prototype will be done.

Exclusion Criteria: Known thrombocytopenia of <50,000 platelets/µl (risk of mild bleeding). No other adult patients will be specifically excluded.

POSSIBLE BENEFITS

There is no direct benefit to the participants, but we hope to provide a new resource to areas with critical shortages of Covid-19 sample collection kits.

POSSIBLE RISKS AND ANALYSIS OF RISK/BENEFIT RATIO

The need for the viral diagnostic testing will be determined by clinicians as part of their conventional evaluation without regard to this protocol. There is minimal risk to subjects. The primary risks are temporary minor discomfort and minimal nasal bleeding.

RECRUITMENT AND CONSENT PROCEDURES

Recruitment: Patients who have been identified as needing evaluation for Covid-19 using a control swab will be told about the option to provide an additional experimental swab test by the treating clinical staff member. To minimize the spread of Covid-19 and conserve on PPE, the team members will not see the potential participant in person.

Consent: Patients who have been identified as needing the standard viral collection test will be asked by the treating clinician if they are willing to have an additional experimental swab test. Treating clinicians will not be added to the research staffing form as swab testing is a part of their standard clinical role at the hospital. The patient will be given a research information sheet which will provide contact information for the study team. Patients with questions may speak to the study team by phone or email for clarifications. To minimize the spread of Covid-19, the study staff will not see the potential participant in person. Additionally, written informed consent is not necessary as the study is minimal risk and written consent requires paper in the clinical area, which increases the risk of disease spreading.

Participants can withdraw at any time. Participants who withdraw will continue to receive conventional care.

Subject Protection: No subject will be influenced by the study team to participate in this trial.

STUDY LOCATION

Privacy: Recruitment will occur in private patient rooms or similar private context.

Potential participants will be given the research information sheet by treating clinical personnel already providing conventional care. Participants will be able to call or email the study team to ask questions or address concerns about the study.

Appropriate members of the study team are already credentialed and can access the participants’ electronic medical records.

Specimen testing will be done at the BIDMC clinical lab.

Physical Setting: The study recruitment and specimen collection will occur at departments where testing is occurring at BIDMC.

DATA SECURITY

Data will be collected on electronic data collection forms which will be securely stored on firewall-protected servers at the sites, and can only be accessed by the site study team. All study staff will be credentialed for research. With an exception of MRN, the data will not contain identifiers. Rather, participants will be assigned a unique identifier. Only de-identified data will be shared with the coordinating site/sponsor. Data will be emailed securely using Excel spreadsheets.

The study will evaluate the performance of a novel sample collection swab. The results will be not shared with the patients or the treating clinicians and will not be part of the patient’s health record.

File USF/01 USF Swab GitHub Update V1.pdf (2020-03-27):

### USF Lab Nasal Swab Testing Summary

This study was conducted parallel to the work from Dr. Ramy Arnaout’s BIDMC team and their excellent work. Both testing centers were blind to each other’s results. We all came to similar conclusions.

BIDMC tested several different materials and several different swab tip geometries. Please see the summary of their results here: https://github.com/HMS‐RIC/Covid19‐NP‐Swab/blob/master/Results/README.md

USF results as follows:

Geometries

USF created several geometries before one was settled on. The tip geometry design was a “cat‐tailed” tip at 15 mm in length and with at 4 mm diameter.


The shaft total (including tip) is 1.5 mm neck, a 2.5 mm handle and a 2 mm break point. The break point is located 70 mm from the tip. We also have an alternate design with two break points, one at 40 mm and one at 80 mm.

There is not a conclusive “best.” Per Dr. Arnaout’s results almost all geometries and materials tested passed. Key point being your design and material does not interfere with the PCR test. It should collect enough material to conduct the test. It should also be flexible and strong. At all costs, avoid sharp tips and edges so the mucosa of the nasopharynx is not damaged.

USF Material

We are printing our swabs with Formlabs Surgical Guide and following their post‐processing indications for IPA cleaning and UV‐curing. We are also following their indications for autoclaving. We are using the Formlabs Form2 and Form3 printers and Surgical Guide resin as it is what we have on hand.

Sample testing

To test the swab’s retention/retrieval comparison, we used 1 ml of synthetic sputum that was spiked with 10 PFU of RSV. We compared the 3D printed swab’s performance against a synthetic polyester swab. 3D printed swabs were as effective as current spun polyester swabs. Dr. Michael Teng, USF

Leeching testing

Tubes were incubated for 24 and 48 hours at 4 degrees C. There was no effect on the PCR. Leeching is not an issue for up to two days. We are continuing this test for 72 hours. Dr. Michael Teng, USF

Structural performance

Our model resists breakage from torsion forces (the kind typical seen while collecting a nasopharyngeal swab). The neck is flexible. The breakpoints break as designed when applied with a perpendicular force.

Field Testing

USF is currently expanding their local IRB to a WIRB to include testing at multiple sites. This expansion will allow for multiple institutions to participate in the research study. We have been in contact with several institutions to include them on the WIRB.

We want to thank everyone for the hard work at your respective institutions. We are impressed with the call to arms and how everyone showed up.

If you do happen to be using the patent pending USF designed swab, please credit as appropriate.

March 26, 2020 4:21 PM EST

Filename: | USF Swab GitHub Update.docx
Directory: | C:\Users\Jonathan\Desktop
Template:
C:\Users\Jonathan\AppData\Roaming\Microsoft\Templates\Normal.dot m
Title:
Subject:
Author: | Ford, Jonathan
Keywords:
Comments:
Creation Date: | 3/26/2020 3:20:00 PM
Change Number: | 3
Last Saved On: | 3/26/2020 4:26:00 PM
Last Saved By: | Ford, Jonathan
Total Editing Time: | 56 Minutes
Last Printed On: | 3/26/2020 4:27:00 PM
As of Last Complete Printing
Number of Pages: 2
Number of Words: 436 (approx.)
Number of Characters: 2,489 (approx.)

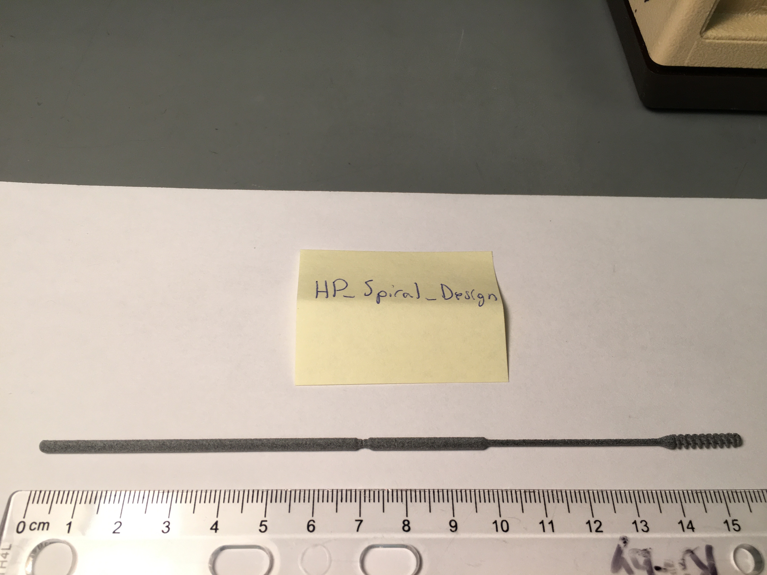
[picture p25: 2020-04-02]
BIDMC/img/HP/HP_Spiral_Design.jpg

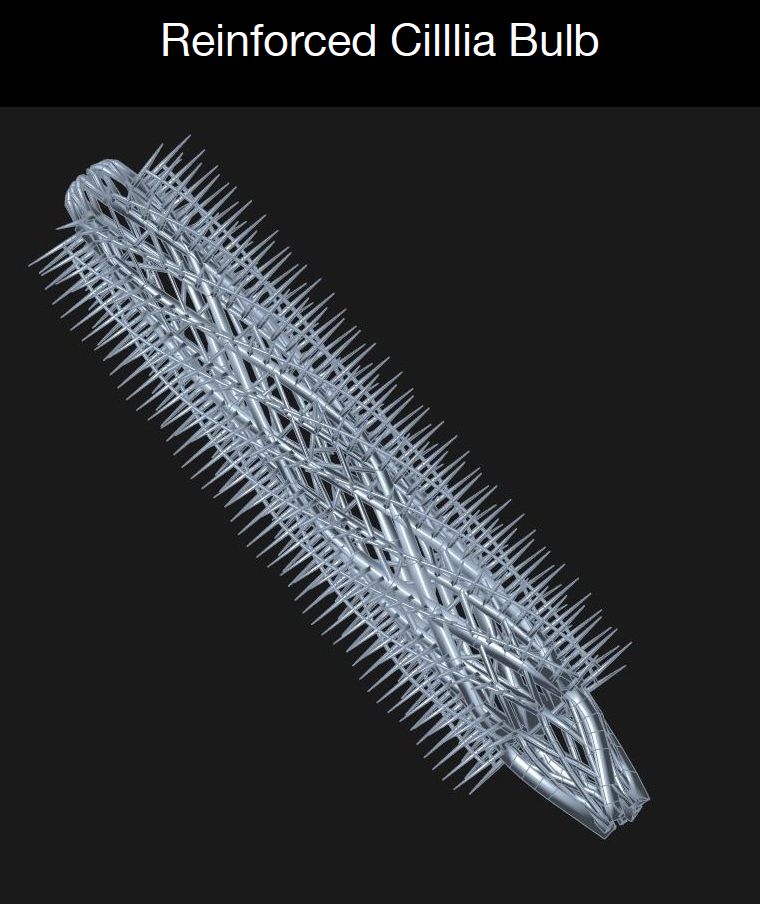
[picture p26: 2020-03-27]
BIDMC/img/OPT_industries/OPTIndustries_full_Swab_design.png

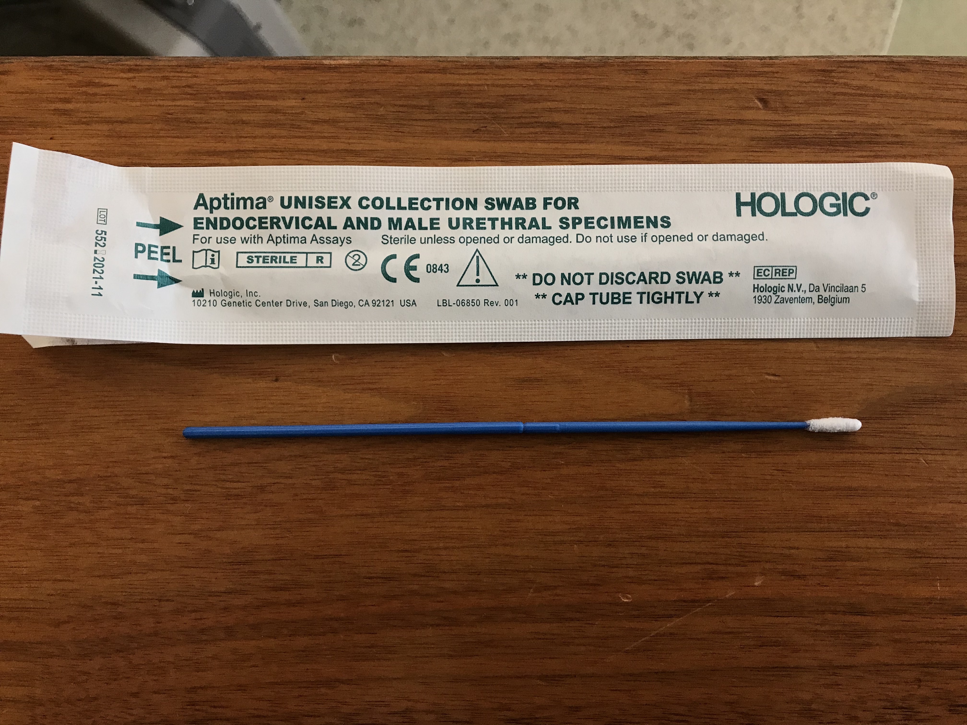
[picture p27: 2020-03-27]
BIDMC/img/Aptima/aptima_unisex_collection_swab_for_endocervical_and_male_urethral_specimena.JPG

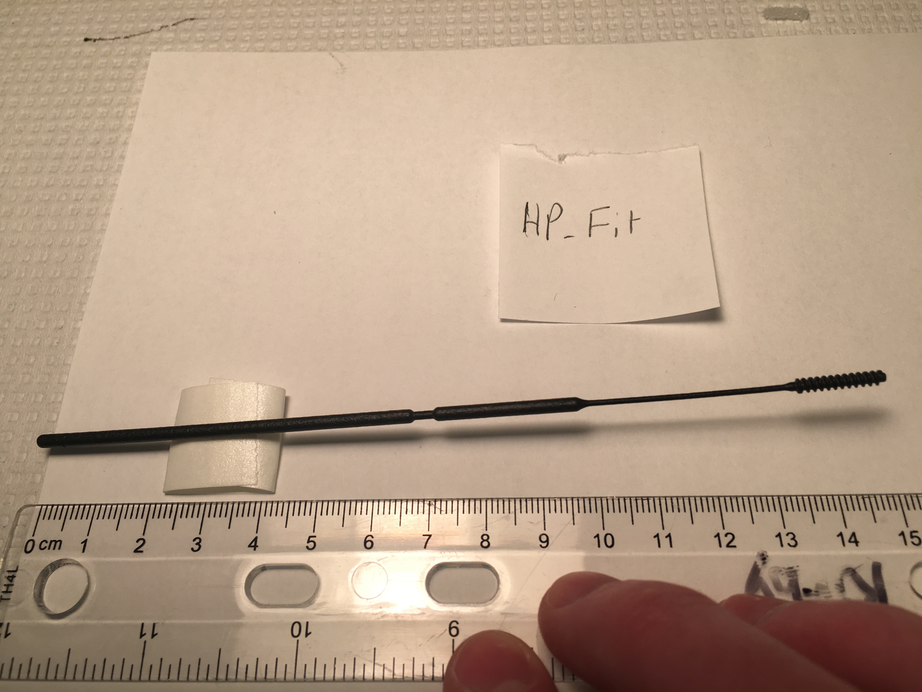
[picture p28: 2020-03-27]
BIDMC/img/HP/HP_Fit.jpg

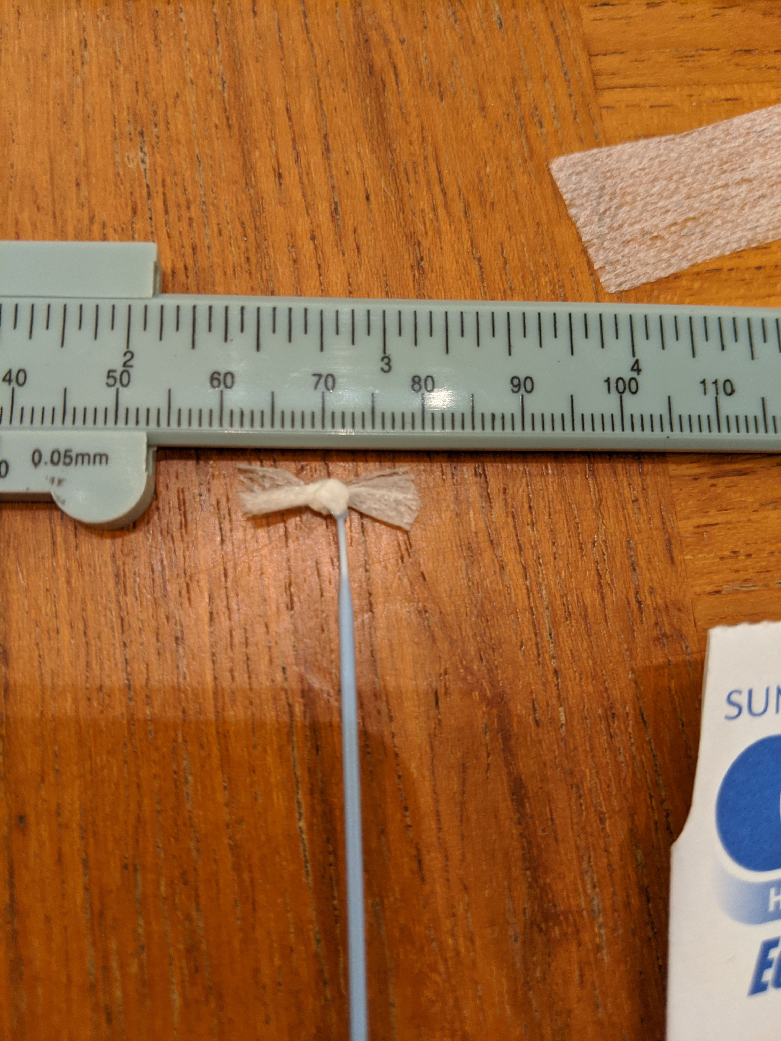
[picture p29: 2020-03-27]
BIDMC/img/Jenny/DIYswab/loop_and_knot dimension_2.6mm.jpg

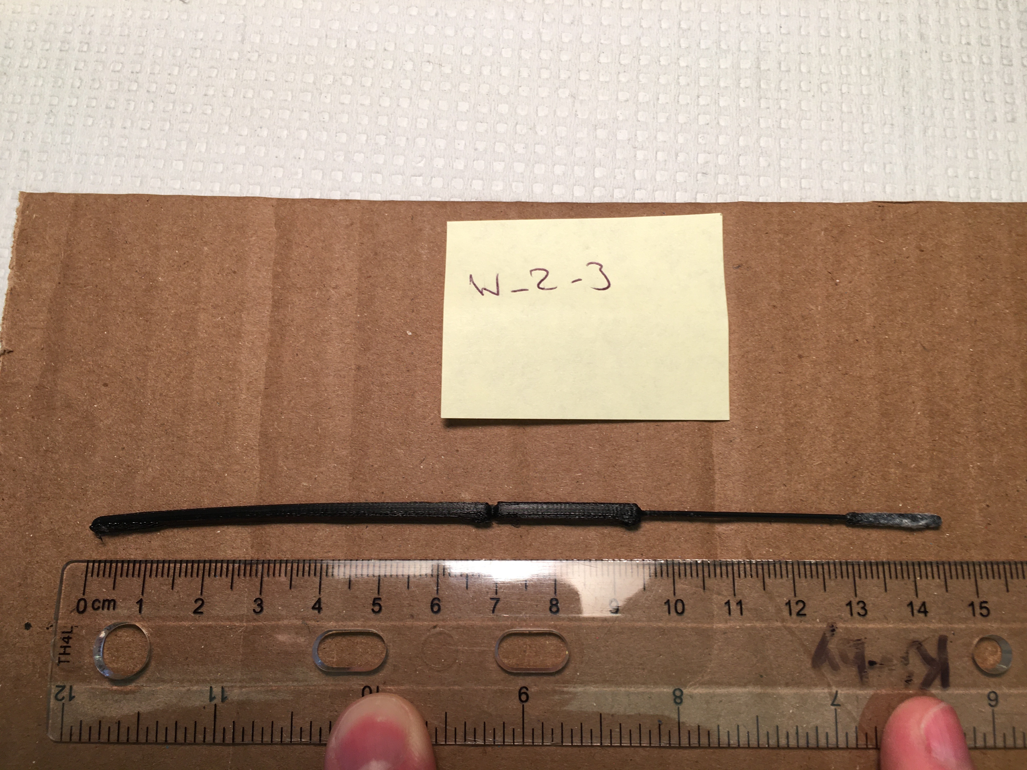
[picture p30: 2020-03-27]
BIDMC/img/Wyss/W_2_3.jpg

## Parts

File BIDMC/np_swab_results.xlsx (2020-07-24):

ID | Description | Date of test | Test site | Picture | Material | Process | Creator (contact info and company) | Link to stl and cad files | Test 1: Expert evaluation by 2 ID physicians | Test 2: Collection sufficiency | Test 3: PCR compatibility | Test 4: 24hrs Post autoclave. Bend test | Notes
This is a unique identifier, ideally including the source's name |  |  | E.g., BIDMC | Please take a high-resolution picture of the entire item provided. | Please describe all (known) materials in the bulb head, including plastic, any adhesive, and any flock | Please include a brief description of the design process that an expert would understand well enough to reproduce. For repurposed swabs, write "commercial." | How to contact the creator for questions/further development | Please send .stl and CAD files, which we will post. | If passes, write "Pass". If fails, write "Fail" and give a brief reason why. Should be filled out by someone who has experience actually using NP swabs in a clinical context. Please leave the name of this person. | If a Gram stain of the (inner) cheek made from the swab shows material broadly consistent with our control, then write "Pass". If not, "Fail" and give reason (too abrasive, did not pick up material, etc.) Note: BIDMC protocol does not include adding fluid. | As above, "Pass" vs. "Fail". Please indicate the protocol used. You can post the protocol in the Testing/ directory, and link to it here
Puritan Sterile polyester-tipped applicators 25-806 1PD |  | 2020-03-22 | BIDMC | https://github.com/rarnaout/Covidswab/tree/master/BIDMC/img/Puritan/puritan_sterile_polyester_tipped_applicator_25-805_1PD.png | Polyester tip | Commercial | Puritan | NA | Did not pass | Not done |  |  | (tip diameter too large)
Fisher polyester-tipped applicators 22363164 |  | 2020-03-22 | BIDMC | https://github.com/rarnaout/Covidswab/tree/master/BIDMC/img/Fisher/fisher_polyester_tipped_applicators_22363164.png | Polyester tip | Commercial | Fisher | NA | Did not pass | Not done |  |  | (tip diameter too large)
Puritan sterile foam tipped applicator 25-1506 1PF |  | 2020-03-22 | BIDMC | https://github.com/rarnaout/Covidswab/tree/master/BIDMC/img/Puritan/puritan_sterile_foam_tipped_applicator_25-1506_1PF.png |  | Commercial | Fisher | NA | Pass | Pass | Pass |  | (but tip diameter large, would be difficult to use)
Copan BD ESwab collection and transport system 220532 |  | 2020-03-22 | BIDMC | https://github.com/rarnaout/Covidswab/tree/master/BIDMC/img/Copan_BD/copan_BD_ESwab_collection_and_transport_system_220532.png |  | Commercial | Fisher | NA | Pass | Pass
Copan ESwab 220245 |  | 2020-03-22 | BIDMC | NA |  | Commercial | Fisher | NA |  |  | Pass
Hologic Aptima LBL-06850 |  | 2020-03-22 | BIDMC | Pending |  | Commercial | Fisher | NA | Pass |  | Pass |  | (but tip diameter large)
Jifei "Carbon" (internal ID, *not* Carbon3D the company) |  | 2020-03-22 | BIDMC | (meth)acrylated urethane photopolymer |  |  | OPT Industries (Jifei Ou) |  |  | Pass | Pass
Jifei Material 2 |  | 2020-03-22 | BIDMC | (meth)acrylated urethane photopolymer | Material 2 |  | OPT Industries (Jifei Ou) |  | NOT SWAB MATERIAL ONLY | NOT SWAB MATERIAL ONLY | Pass
Nilson |  | Mach 20,2020 | BIDMC |  | Rose-print1 | Printed usign E Guide 2.0, cleaned in 99% IPA, 2000 Flash cure with ottoflash unit |  |  |  |  | Pass
Formlabs - Honey Tip |  | 2020-03-22 | BIDMC | https://github.com/rarnaout/Covidswab/tree/master/BIDMC/img/FormLabs/honeydipper.png |  |  | FormLabs (Craig Brody) |  | Did not pass | Pass | Pass |  | (shaft needs to be smooth; material too brittle)
Formlabs - Spiral Tip |  | 2020-03-22 | BIDMC | https://github.com/rarnaout/Covidswab/tree/master/BIDMC/img/FormLabs/surgical_guide_technical_data_sheet_en.pdf |  |  | FormLabs (Craig Brody) |  | Did not pass | Did not pass (material did not transfer to slide?) | Pass |  | (shaft needs to be smooth; material too brittle)
Formlabs - Bristle Tip |  | 2020-03-22 | BIDMC | https://github.com/rarnaout/Covidswab/tree/master/BIDMC/img/FormLabs/bristles.png |  |  | FormLabs (Craig Brody) |  | Did not pass | Did not pass (material did not transfer to slide?) | Pass |  | (shaft needs to be smooth; material too brittle)
Formlabs - Dental LT clear (Bristle, Honey tips) |  | 2020-03-22 | BIDMC | https://github.com/rarnaout/Covidswab/tree/master/BIDMC/img/FormLabs/DentalLT.JPG |  |  | FormLabs (Craig Brody) |  | Did not pass |  |  |  | (tip needs to be more flexible - will abutt posterior nasopharynx, but flexibility of NP neck, handle/body still needs to be more smooth)
Formlabs - Dental SG (Fern tip) |  | 2020-03-22 | BIDMC | https://github.com/rarnaout/Covidswab/tree/master/BIDMC/img/FormLabs/SG.JPG |  |  | FormLabs (Craig Brody) |  | Did not pass | Pass |  |  | (tip needs to be more flexible - will abutt posterior nasopharynx, but flexibility of NP neck, handle/body still needs to be more smooth)
Formlabs - Grey Pro (Spiral, Honey, Bristle) |  | 2020-03-22 | BIDMC | https://github.com/rarnaout/Covidswab/tree/master/BIDMC/img/FormLabs/GreyPro.JPG |  |  | FormLabs (Craig Brody) |  | Did not pass |  |  |  | (material brittle, tip needs to be more flexible - will abutt posterior nasopharynx, but flexibility of NP neck, handle/body still needs to be more smooth)
Formlabs - Durable (Fern, Honey, Bristle) |  | 2020-03-22 | BIDMC | https://github.com/rarnaout/Covidswab/tree/master/BIDMC/img/FormLabs/Durable.JPG |  |  | FormLabs (Craig Brody) |  | Did Not Pass | Pass (All but Bristle tip -very few cells with that tip) | Pass |  | *Tested this material as was closest to desirable design although did not pass Test . (Flexibility of tip appropriate, but neck for these designs is too elastic, difficult to pass middle turbinate, and folds in external nasal cavity)
Formlabs Tough (Spiral, Bristle, Honey, Fern) |  | 2020-03-23 | BIDMC | https://github.com/rarnaout/Covidswab/tree/master/BIDMC/img/FormLabs/tough.JPG |  |  | FormLabs (Craig Brody) |  | Did not pass |  |  |  | (tip needs to be more flexible - will abutt posterior nasopharynx)
Formlabs Dental Model (Honey, Bristle) |  | 2020-03-24 | BIDMC | https://github.com/rarnaout/Covidswab/tree/master/BIDMC/img/FormLabs/model.JPG |  |  | FormLabs (Craig Brody) |  | Did not pass |  |  |  | (tip needs to be more flexible - will abutt posterior nasopharynx, and material too brittle)
Formlabs Tough 1500 (Spiral, Brittle) |  | 2020-03-25 | BIDMC | https://github.com/rarnaout/Covidswab/tree/master/BIDMC/img/FormLabs/tough1500.JPG |  |  | FormLabs (Craig Brody) |  | Did not pass |  |  |  | (tip needs to be more flexible - will abutt posterior nasopharynx)
Formlabs Tough - Tip 4 (Spiral, Bristle, Honey, Fern) |  | 2020-03-26 | BIDMC | https://github.com/rarnaout/Covidswab/tree/master/BIDMC/img/FormLabs/tough.JPG |  |  | FormLabs (Craig Brody) |  | Did not pass |  |  |  | (tip needs to be more flexible - will abutt posterior nasopharynx)
Harvard Army |  | 2020-03-22 | BIDMC | https://github.com/rarnaout/Covidswab/tree/master/BIDMC/img/Harvard_army/new_skin.png |  |  | Army (Kit Parker) |  | Did not pass | "New Skin" passes; others did not pass (too little material) |  |  | (3 glues used - Locktite, Dermabond, New skin) (material too brittle)
Harvard Army Ultem |  | 2020-03-23 |  | https://github.com/rarnaout/Covidswab/tree/master/BIDMC/img/Harvard_army/ultem.JPG |  |  | Army (Kit Parker) |  | Did not pass |  |  |  | (material too brittle, tip inflexible
Harvard Army Onyx |  | 2020-03-23 |  | https://github.com/rarnaout/Covidswab/tree/master/BIDMC/img/Harvard_army/onyx.JPG |  |  | Army (Kit Parker) |  | Did not pass |  |  |  | (tip too inflexible)
Harvard Army Polyjet |  | 2020-03-23 |  |  |  |  | Army (Kit Parker) |  | Pass | (not tested, only one swab which was tested for PCR) | Pass
W1 |  | 2020-03-22 | BIDMC | https://github.com/rarnaout/Covidswab/tree/master/BIDMC/img/Wyss/wyss_w1.png | rayon, fiber, silicon glue, polycarbonate probe |  | Wyss Institute (Adama Sesay) |  | Pass | Pass | Pass
W2 |  | 2020-03-22 | BIDMC | https://github.com/rarnaout/Covidswab/tree/master/BIDMC/img/Wyss/wyss_w2.png | nylon fiber (0.75µm), silicon glue, polycarbonate probe |  | Wyss Institute (Adama Sesay) |  | Did not pass | Did not pass (No visible cells or bacteria) |  |  | (needs a tapered, flexible end)
W3 |  | 2020-03-22 | BIDMC | https://github.com/rarnaout/Covidswab/tree/master/BIDMC/img/Wyss/wyss_w3.png | rayon fiber, silicon glue, nylon probe |  | Wyss Institute (Adama Sesay) |  | Pass | Did not pass (very few cells/bacteria)
W4 |  | 2020-03-22 | BIDMC | https://github.com/rarnaout/Covidswab/tree/master/BIDMC/img/Wyss/wyss_w4.png | rayon immfiber, silicon glue, commercial straw |  | Wyss Institute (Adama Sesay) |  | Did not pass | Pass |  |  | (needs a tapered, flexible end)
W5 |  | 2020-03-22 | BIDMC | https://github.com/rarnaout/Covidswab/tree/master/BIDMC/img/Wyss/wyss_w5.png | nylon fiber (0.75µm), nylon probe, silicon glue |  | Wyss Institute (Adama Sesay) |  | Pass | Pass
W6 |  | 2020-03-22 | BIDMC | https://github.com/rarnaout/Covidswab/tree/master/BIDMC/img/Wyss/wyss_w6.png | polycarbonate 3D-printed probe |  | Wyss Institute (Adama Sesay) |  | Pass | Pass
W7 |  | 2020-03-22 | BIDMC | https://github.com/rarnaout/Covidswab/tree/master/BIDMC/img/Wyss/wyss_w7.png | nylon 3D-printed probe |  | Wyss Institute (Adama Sesay) |  | Pass | Pass
W8 |  | 2020-03-22 | BIDMC | https://github.com/rarnaout/Covidswab/tree/master/BIDMC/img/Wyss/wyss_w8.png | nylon fiber (0.75µm), silicon glue, polycarbonate probe |  | Wyss Institute (Adama Sesay) |  | Pass | Pass
VWR 1ul loop + pellon p45 fabric knot - Jenny |  | 2020-03-22 | HH (Seattle) | https://github.com/rarnaout/Covidswab/tree/master/BIDMC/img/Jenny/DIYswab/ | polystyrene loop and pellon P45 fabric | see https://github.com/HMS-RIC/Covid19-NP-Swab/wiki/DIY-swab-assembly | Jenny |  | Pass | need review of smear pics |  |  | (doctor/swabber was able to use 5mm loop, newer iteration is <3mm) - Jenny
USF_1_1 | Rings w/ medium spacing distance | 2020-03-23 | BIDMC | https://github.com/rarnaout/Covidswab/tree/master/BIDMC/img/USF/USF1-1.jpg |  |  | HP (Rick Fulop; ricfulop@desktopmetal.com) |  | Did not pass | Pass | Pass |  | (tip is too sharp but appropriately flexible, but body design (flexibility of neck and stiffness of handle is appropriate). There is a fine powder on these materials that we are concerned could be health hazard if aspirated
USF_1_2 | Rings w/ low spacing distance |  |  | https://github.com/rarnaout/Covidswab/tree/master/BIDMC/img/USF/USF1-2.JPG |  |  | HP (Rick Fulop; ricfulop@desktopmetal.com) |  | Did not pass | Pass | (presume pass if same material as USF1_1) |  | (tip is too sharp but stiff/brittle, but body design (flexibility of neck and stiffness of handle is appropriate). There is a fine powder on these materials that we are concerned could be health hazard if aspirated
USF_1_3 | Rounded tip w/ protrusions |  |  | https://github.com/rarnaout/Covidswab/tree/master/BIDMC/img/USF/USF1-3.JPG |  |  | HP (Rick Fulop; ricfulop@desktopmetal.com) |  | Did not pass | Pass | (presume pass if same material as USF1_1) |  | (tip is too sharp and stiff, but body design (flexibility of neck and stiffness of handle is appropriate). There is a fine powder on these materials that we are concerned could be health hazard if aspirated
USF_1_4 | Screw; finely threaded |  |  | https://github.com/rarnaout/Covidswab/tree/master/BIDMC/img/USF/USF1-4.JPG |  |  | HP (Rick Fulop; ricfulop@desktopmetal.com) |  | Did not pass | Pass | (presume pass if same material as USF1_1) |  | (tip is too sharp and stiff/brittle, but body design (flexibility of neck and stiffness of handle is appropriate). There is a fine powder on these materials that we are concerned could be health hazard if aspirated
USF_1_5 | Screw; medium thread |  |  | https://github.com/rarnaout/Covidswab/tree/master/BIDMC/img/USF/USF1-5.JPG |  |  | HP (Rick Fulop; ricfulop@desktopmetal.com) |  | Did not pass | Pass | (presume pass if same material as USF1_1) |  | (tip is too sharp but we like the spring and how flexible it is, but body design (flexibility of neck and stiffness of handle is appropriate). There is a fine powder on these materials that we are concerned could be health hazard if aspirated
USF_1_6 | Screw;large thread | 2020-03-23 |  | https://github.com/rarnaout/Covidswab/tree/master/BIDMC/img/USF/USF1-6.JPG |  |  | HP (Rick Fulop; ricfulop@desktopmetal.com) |  | Did not pass | Pass | (presume pass if same material as USF1_1) |  | (tip is too sharp but we like the spring and how flexible it is, but body design (flexibility of neck and stiffness of handle is appropriate). There is a fine powder on these materials that we are concerned could be health hazard if aspirated
HP_H | HP swabs with holes | March 23,2020 | BIDMC | https://github.com/rarnaout/Covidswab/tree/master/BIDMC/img/HP/HPH.JPG |  |  | HP (LihuA Zhao; Zhao, Lihua <lihua.zhao@hp.com) |  | **Conflicting Results** Pass per Jenny Hu 032320 Not pass per BIDMC: | **Conflicting Results** Pass per Jenny Hu 032320 (collected a few cells/bacteria from cheek swab then rubbing directly on slides; better results from rinsing the tip with 150ul of buffer then transfering liquid to slide). Not pass per BIDMC protocol (no elution); very few cells collected |  |  | Doing some more mechanical measurements/testing this afternoon then my doctor friend will stop by after work and I'll do NP swabs with Copan, HP_H, HP_NH, VWRloop+facric. Will smear swabs directly on slides then try rinsing and looking at rinse liquid for cells/bacteria. per Jenny Hu 032320: doctor swabber would like the shaft to be longer but likes the shaft flexibility and tip size. : tip not very flexible and too sharp at the end
HP_NH | HP swabs without holes | 2020-03-23 | BIDMC | https://github.com/rarnaout/Covidswab/tree/master/BIDMC/img/HP/HPNP.JPG |  |  | HP (LihuA Zhao; Zhao, Lihua <lihua.zhao@hp.com) |  | **Conflicting Results** Pass per Jenny Hu 032320:. Not pass per BIDMC: | **Conflicting Results** Pass per Jenny Hu 032320 (collected a few cells/bacteria from cheek swab then rubbing directly on slides; better results from rinsing the tip with 150ul of buffer then transfering liquid to slide). Not pass per BIDMC protocol (no elution); very few cells collected | Pass |  | doctor swabber would like the shaft to be longer but likes the shaft flexibility and tip size. tip not very flexible and too sharp at the end
C_1 | Carbon 3D bag 1 | 2020-03-23 | BIDMC | https://github.com/rarnaout/Covidswab/tree/master/BIDMC/img/Carbon/C1.JPG |  |  | Carbon 3D ( Hardik Kabaria <hardik@carbon3d.com) |  | Pass | Pass | Pass |  | (good stiffness of handle, and flexible tip), tapered more flexible neck would be better
C_2 | Carbon 3D bag 2 | 2020-03-23 | BIDMC | https://github.com/rarnaout/Covidswab/tree/master/BIDMC/img/Carbon/C2.JPG |  |  | Carbon 3D ( Hardik Kabaria <hardik@carbon3d.com) |  | Pass | Pass |  |  | (good stiffness of material, and flexible tip), tapered more flexible neck would be better
P_0 | Swab_test_Wyss | 2020-03-23 | BIDMC | https://github.com/rarnaout/Covidswab/tree/master/BIDMC/img/Gorelik/P0.JPG | PA12 |  | Empire Group. (Pavel Gorelik; oreshki@gmail.com ) |  | Did not pass | Pass |  |  | - tip needs to be more flexible, but stiffness of neck and elasticity of material appropriate)
P_1 | Solid_Circular | 2020-03-23 | BIDMC | https://github.com/rarnaout/Covidswab/tree/master/BIDMC/img/Gorelik/P1.JPG | PA12 |  | Empire Group. (Pavel Gorelik; oreshki@gmail.com ) |  | Did not pass | Pass |  |  | (tip too sharp, appropriately flexible, but would make tip end less jagged)
P_2 | Spring_Circular | 2020-03-23 | BIDMC | https://github.com/rarnaout/Covidswab/tree/master/BIDMC/img/Gorelik/P2.JPG | PA12 |  | Empire Group. (Pavel Gorelik; oreshki@gmail.com ) |  | Did not pass | Pass | Pass |  | (tip too sharp but more appropriately flexible, but would make tip end less jagged)
P_3 | Spring_Flat | 2020-03-23 | BIDMC | https://github.com/rarnaout/Covidswab/tree/master/BIDMC/img/Gorelik/P3.JPG | PA12 |  | Empire Group. (Pavel Gorelik; oreshki@gmail.com ) |  | Pass - | Pass |  |  | tip is softer/flexible, and stiffness of neck and elasticity of material appropriate)
P_4 | Solid_Flat | 2020-03-23 | BIDMC | https://github.com/rarnaout/Covidswab/tree/master/BIDMC/img/Gorelik/P4.JPG | PA12 |  | Empire Group. (Pavel Gorelik; oreshki@gmail.com ) |  | Did not pass | Pass |  |  | (tip too sharp/stiff, body design appropriate)
P_5 | Swab_Concentric | 2020-03-23 | BIDMC | https://github.com/rarnaout/Covidswab/tree/master/BIDMC/img/Gorelik/P5.JPG | PA12 |  | Empire Group. (Pavel Gorelik; oreshki@gmail.com ) |  | Pass | Pass |  |  | (tip more appropriately flexible, but would make tip end less jagged)
P_6 | Swab_concentric_bigger_pitch | 2020-03-23 | BIDMC | https://github.com/rarnaout/Covidswab/tree/master/BIDMC/img/Gorelik/P6.JPG | PA12 |  | Empire Group. (Pavel Gorelik; oreshki@gmail.com ) |  | Pass | Pass |  |  | (tip more appropriately flexible, but would make tip end less jagged)
P_7 | Swab_test_head_4_wyss | 2020-03-23 | BIDMC | https://github.com/rarnaout/Covidswab/tree/master/BIDMC/img/Gorelik/P7.JPG | PA12 |  | Empire Group. (Pavel Gorelik; oreshki@gmail.com ) |  | Pass for tip head
J_1 | flexible swab w/ case | March 24th, 2020 | BIDMC | https://github.com/rarnaout/Covidswab/tree/master/BIDMC/img/OPT_industries/J_1.JPG | methylacrylic urethane |  | opticalindustries, jifei jifei@optindustries.com |  | Pass but design too short | Pass | passed
USF_2_1 | swab w/ fine nubs | March 24th, 2020 | BIDMC | https://github.com/rarnaout/Covidswab/tree/master/BIDMC/img/USF/USF_2_1.JPG |  |  | HP (Rick Fulop; ricfulop@desktopmetal.com) |  | Did not pass | Pass | Pass |  | (tip too sharp and should be more flexible, but body design is appropriate)
USF_2_2 | swab w/ finely spaced rings | Marh 24th, 2020 | BIDMC | https://github.com/rarnaout/Covidswab/tree/master/BIDMC/img/USF/USF_2_2.JPG |  |  | HP (Rick Fulop; ricfulop@desktopmetal.com) |  | Did not pass | Pass |  |  | (tip too sharp and but apporpirately flexible, but body design is appropriate)
B_1 | swab w/very fine nubs | March 24th, 2020 | BIDMC | https://github.com/rarnaout/Covidswab/tree/master/BIDMC/img/Baker/B_1.JPG |  |  | Daniel Baker |  | Did not pass | Pass | Pass |  | (tip is too sharp and ideally more flexible tip, but body design is appropriate)
S_1 | Swab w/ thick thread | March 24th, 2020 | BIDMC | https://github.com/rarnaout/Covidswab/tree/master/BIDMC/img/Seriano/S_1.JPG |  |  | David Seriano |  | Did not pass | Pass | Pass |  | (tip is too sharp, but apporpiately flexible and body design is appopriate)
S_2 | swab w/ fine spring | March 24th | BIDMC | https://github.com/rarnaout/Covidswab/tree/master/BIDMC/img/Seriano/S_2.JPG |  |  | David Seriano |  | Did not pass | Pass |  |  | (tip is too sharp, but very flexible, perhaps too flexible, S1 may be better, and body design is appopriate)
S_3 | swab w/ fine thread | March 24th | BIDMC | https://github.com/rarnaout/Covidswab/tree/master/BIDMC/img/Seriano/S_3.jpg |  |  | David Seriano |  | Did not pass | Pass |  |  | (tip is too sharp, and body design is appopriate)
S_4 | swab w/finely speaced rings | March 24th | BIDMC | https://github.com/rarnaout/Covidswab/tree/master/BIDMC/img/Seriano/S_4.JPG |  |  | David Seriano |  | Did not pass | Pass |  |  | (tip is too sharp, and body design is appopriate, best design of the S-series in terms of head softness)
S_5 | swab w/ low ring spacing | March 24th | BIDMC | https://github.com/rarnaout/Covidswab/tree/master/BIDMC/img/Seriano/S_5.JPG |  |  | David Seriano |  | Did not pass | Pass |  |  | (tip is too sharp, and body design is appopriate)
S_6 | swab w/fine rings | March 24th | BIDMC | https://github.com/rarnaout/Covidswab/tree/master/BIDMC/img/Seriano/S_6.JPG |  |  | David Seriano |  |  | Pass
FT_1 | Foam Swab. Pt: HT1171B | March 24th, 2020 | BIDMC | https://github.com/rarnaout/Covidswab/tree/master/BIDMC/img/Foamtec/FT_1.JPG |  |  | Foamtec International; Michael Strauss |  | Did not pass | Did not pass (not many cells collected) |  |  | (diameter of tip too large, flexible bendable neck would be better)
FT_2 | Foam Swab. Pt: HT1501T2-5 | March 24th, 2020 | BIDMC | https://github.com/rarnaout/Covidswab/tree/master/BIDMC/img/Foamtec/FT_2.JPG |  |  | Foamtec International; Michael Strauss |  | Did not pass | Did not pass (not many cells collected) |  |  | (diameter of tip too large, flexible bendable neck would be better)
FT_3 | Foam. Pt. HT1501TC-5 | March 24th, 2020 | BIDMC | https://github.com/rarnaout/Covidswab/tree/master/BIDMC/img/Foamtec/FT_3.JPG |  |  | Foamtec International; Michael Strauss |  | Did not pass | Did not pass (not many cells collected) |  |  | (diameter of tip too large, flexible bendable neck would be better)
FT_4 | Foam Swab. Pt: HT1001-5 | March 24th, 2020 | BIDMC | https://github.com/rarnaout/Covidswab/tree/master/BIDMC//img/Foamtec/FT_4.JPG |  |  | Foamtec International; Michael Strauss |  | Did not pass | Did not pass (not many cells collected) |  |  | (diameter tip, diameter of tip too large, flexible bendable neck would be better)
EV_1 | DOWEL. For material testing | March 24th, 2020 | BIDMC |  | PCA 2000. 10 minutes. 100% |  | EnvisionTEC. Al Siblani. asiblani@envisiontec.com |  |  |  | passed
EV_2 | DOWEL. For material testing | March 24th, 2020 | BIDMC |  | PCA100 w/nitrogen | 2x10seconds w/nitrogen | EnvisionTEC. Al Siblani. asiblani@envisiontec.com |  |  |  | off for testing
EV_3 | DOWEL. For material testing | March 24th, 2020 | BIDMC |  | PCA 100 w/nitrogen | 2x30seconds UV w/nitrogen | EnvisionTEC. Al Siblani. asiblani@envisiontec.com |  |  |  | off for testing
EV_4 | DOWEL. For material testing | March 24th, 2020 | BIDMC |  | PCA 100 w/nitrogen | 2x20seconds w/nitrogen | EnvisionTEC. Al Siblani. asiblani@envisiontec.com |  |  |  | off for testing
PVA | Chemical for material testing. Cas: 9002-89-5 | March 25th, 2020 | BIDMC |  | Polly(Vinyl Alcohol) |  | Sigma-Aldrich. Adama; Wyss |  |  |  | passed
Fil_Flt | White filament (for material testing) | March 25h, 2020 | BIDMC |  | 3DF-2 (Raw) (Polyurethane + PVA) |  | Adama; Wyss |  |  |  | passed
Fil_Lay | White filament (for material testing) | March 25th, 2020 | BIDMC |  | 3DF-1 (polyurethane + PVA) |  | Adama Sesay, Wyss Institude |  |  |  | passed
Sc_M | Jar filled with white substance | March 25th, 2020 | BIDMC |  | Scotch Magic Tape |  | 3M. dropped off by Adama Sesay; Wyss Institute |  |  |  | passed
Sc_CC | Jar filled with white substance | March 25th, 2020 | BIDMC |  | Scotch Crystal Clear |  | 3M. dropped off by Adama Sesay; Wyss Institute
W_2_1 | White swab w/ silicon glue and sugar textured head | March 25th, 2020 | BIDMC | https://github.com/rarnaout/Covidswab/tree/master/BIDMC/img/Wyss/W_2_1.jpg | SG1. Silicon glue and sugar |  | Wyss Institute (Adama Shesay) |  | Did not pass | Pass |  |  | (body design is appropriate, but tip/neck is too flexible and seems would not easily pass beyond external nares, seems non-uniform & wasn't sure if there would be scale-up reproducibility issues)
W_2_2 | Black swab w/ silicon glue and sugar textured head | March 25th, 2020 | BIDMC | https://github.com/rarnaout/Covidswab/tree/master/BIDMC/img/Wyss/W_2_2.jpg | SG2. Silicon glue and Sugar |  | Wyss Institute (Adama Shesay) |  | Pass | Pass |  |  | (body design is appropriate, the tip end material seems very absorbent which we like, but the tip would ideally be more flexible, tip seems non-uniform & wasn't sure if there would be scale-up reproducibility issues)
W_2_3 | Rayon and crystal clear glue textured head | March 25th, 2020 | BIDMC | https://github.com/rarnaout/Covidswab/tree/master/BIDMC/img/Wyss/W_2_3.jpg | 3M1. Rayon fiber and scotch crystal clear glue head with polycarbonate swab |  | Wyss Institute (Adama Shesay) |  | Did not pass | Pass |  |  | (tip sharp and inflexible but body design is appropriate, tip seems non-uniform & wasn't sure if there would be scale-up reproducibility issues)
W_2_4 | Rayon and magic tape textured head | March 25th, 2020 | BIDMC | https://github.com/rarnaout/Covidswab/tree/master/BIDMC/img/Wyss/W_2_4.jpg | 3M2. Rayon fiber with scoth magic tape swab head on a nylon swab |  | Wyss Institute (Adama Shesay) |  | Pass | Did not do cheek swab, uncured glue |  |  | (tip is flexible and body design is appropriate)
W_2_5 | Rayon fiber and scotch crysal clear textured head | March 25th, 2020 | BIDMC | https://github.com/rarnaout/Covidswab/tree/master/BIDMC/img/Wyss/W_2_5.jpg | 3M3 Rayon Fiber with scotch crystal clear textured head on nylon swab |  | Wyss Institute (Adama Shesay) |  | Pass | Pass |  |  | (tip is flexible and body design is appropriate, tip seems non-uniform & wasn't sure if there would be scale-up reproducibility issues, also seems stikcy)
W_2_6 | Rayon fiber/ Scotch magnetic tape textured head | March 25th, 2020 | BIDMC | https://github.com/rarnaout/Covidswab/tree/master/BIDMC/img/Wyss/W_2_6.jpg | 3M4 Rayon Fiber/Scotch magic tape textured head on polycarbonate head |  | Wyss Institute (Adama Shesay) |  | Did not pass | Did not do cheek swab, uncured glue |  |  | (tip is sharp and inflexible but body design is appropriate, tip seems non-uniform & wasn't sure if there would be scale-up reproducibility issues)
W_2_7 | Nylon fiber/magic tape | March 25th, 2020 | BIDMC | https://github.com/rarnaout/Covidswab/tree/master/BIDMC/img/Wyss/W_2_7.jpg | 3M5 Nylon Fiber/Magic Tape textured head on polycarbornate swab |  | Wyss Institute (Adama Shesay) |  | Pass | Pass |  |  | (tip would ideally be more flexible but body design is appropriate, tip seems non-uniform & wasn't sure if there would be scale-up reproducibility issues)
W_2_8 | Nylon fiber/magic tape | March 25th, 2020 | BIDMC | https://github.com/rarnaout/Covidswab/tree/master/BIDMC/img/Wyss/W_2_8.jpg | 3M6 Nylon Fiber/magi tape textured head on nylon swab |  | Wyss Institute (Adama Shesay) |  | Pass | Pass |  |  | (tip ideally would be more flexible, but design is appopriate, tip seems non-uniform & wasn't sure if there would be scale-up reproducibility issues)
W_2_9 | Nylon FIber/Crystal Clear | March 25th, 2020 | BIDMC | https://github.com/rarnaout/Covidswab/tree/master/BIDMC/img/Wyss/W_2_9.jpg | 3M_7 Nylon fiber/ crystal clear textured head on a nylon swab |  | Wyss Institute (Adama Shesay) |  | Pass | Pass |  |  | (tip is flexible and body design is appropriate, tip seems non-uniform & wasn't sure if there would be scale-up reproducibility issues)
W_2_10 | Nylon fiber/magic tape | Martch 25th, 2020 | BIDMC | https://github.com/rarnaout/Covidswab/tree/master/BIDMC/img/Wyss/W_2_10.jpg | 3M8 nylon fiber/magic tape texted head on a nylon swab |  | Wyss Institute (Adama Shesay) |  | Pass | Pass |  |  | (tip is more flexible which we like but body design is appropriate, tip seems non-uniform & wasn't sure if there would be scale-up reproducibility issues)
W_2_11 | Nylon FIber/ crytal clear textured head | March 25th, 2020 | BIDMC | https://github.com/rarnaout/Covidswab/tree/master/BIDMC/img/Wyss/W_2_11.jpg | 3M9 nylon fiber w/ crystal clear textured head on polycarb |  | Wyss Institute (Adama Shesay) |  | Did not pass | Pass |  |  | (too sharp and tip too inflexible)
W_2_12 | Sugar on nylon | March 25th, 2020 | BIDMC | https://github.com/rarnaout/Covidswab/tree/master/BIDMC/img/Wyss/W_2_12.jpg | PDMS [sugar on nylon] |  | Wyss Institute (Adama Shesay) |  | Did not pass | Pass | Pass |  | (tip/neck are too flexible we feel like it would get caught in the external nares and not pass deeper well)
EV_2_1 | 3cm rods (for material testing) |  |  | https://github.com/rarnaout/Covidswab/tree/master/BIDMC/img/Envisiontec/EV_2_1.jpg | C 29C |  | EnvisionTEC. Al Siblani. asiblani@envisiontec.com |  | NA |  | passed
C_3 | 4mm voro | March 26th, 2020 | BIDMC | https://github.com/rarnaout/Covidswab/tree/master/BIDMC/img/Carbon/C_3.jpg | keysplint Soft Clear | dreve PCU 90 N2 15 min | Carbon3D. Keshav Swarup |  | Did not pass | Pass | *pass (presumably same material as C!) |  | (tip head too firm, would create a neck for more flexibility at the end, and would put breakpoint from tip head end at least 7-10cm from the end.
C_4 | 3mm voro | March 26th, 2020 | BIDMC | https://github.com/rarnaout/Covidswab/tree/master/BIDMC/img/Carbon/C_4.jpg | keysplint Soft Clear | dreve PCU 90 N2 15 min | Carbon3D. Keshav Swarup |  | Did not pass | Pass | *pass (presumably same material as C!) |  | (tip head too firm, would create a neck for more flexibility at the end, and would put breakpoint from tip head end at least 7-10cm from the end).
C_5 | USF | March 26th, 2020 | BIDMC | https://github.com/rarnaout/Covidswab/tree/master/BIDMC/img/Carbon/C_5.jpg | keysplint Soft Clear | dreve PCU 90 N2 15 min | Carbon3D. Keshav Swarup |  | Did not pass | Did not pass | *pass (presumably same material as C!) |  | (tip head too sharp and stiff although bristeled head may perform better ultmately for specimen capture. Body design is good)
C_6 | long bulb | March 26th, 2020 | BIDMC | https://github.com/rarnaout/Covidswab/tree/master/BIDMC/img/Carbon/C_6.jpg | keysplint Soft Clear | dreve PCU 90 N2 15 min | Carbon3D. Keshav Swarup |  | Pass | Pass | *pass (presumably same material as C!) |  | **likely a good design, the head is longer and flexible and probably can pass deeper as well as pickup more material. (unique design, and may be preferable to others given logner head/more absorption, and flexibility of entire head while maintaining shape well after deformation)
C_7 | 3mm 1.5mm neck | March 26th, 2020 | BIDMC | https://github.com/rarnaout/Covidswab/tree/master/BIDMC/img/Carbon/C_7.jpg | keysplint Soft Clear | dreve PCU 90 N2 15 min | Carbon3D. Keshav Swarup |  | Pass | Pass | *pass (presumably same material as C!) |  | (body design std Copan, tip soft enough)
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

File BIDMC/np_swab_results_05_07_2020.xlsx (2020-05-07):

ID | Description | Date of Test | Test Site | Picture | Material | Process | Creator(contact info and company) | Test 1: Expert Evaluation by 2 ID physicians | Test 2: Collection Sufficiency | Test 3: PCR compatibility | Test 4: 24 hours post autoclave bend test | Notes
C_Na_1 | 5 Nasal Swab tips, with a tapered mesh end and a depth stop | 2020-05-06 | BIDMC |  | Keysplint Soft | Dreve PCU 90 N2 20 minutes | Carbon 3D ( Hardik Kabaria <hardik@carbon3d.com) |  |  | (pressumed pass because it's keysplint soft)
Copan_Nasal_swab | dual swabs with vial filled with a vtm gel (138CQ BD) | 2020-05-06 | BIDMC
CF_Bleached_Rayon_33mm | 33 mm bleached rayon spun around a plastic extrusion | 2020-05-06 | BIDMC |  | rayon and an unpecified (methylcellulose) |  |  |  |  | Pass
CF_rayon_6in | 6 inch rayon swab with hand spun rayon | 2020-05-06 | BIDMC |  | rayon and an unpecified (methylcellulose) |  |  |  |  | Pass

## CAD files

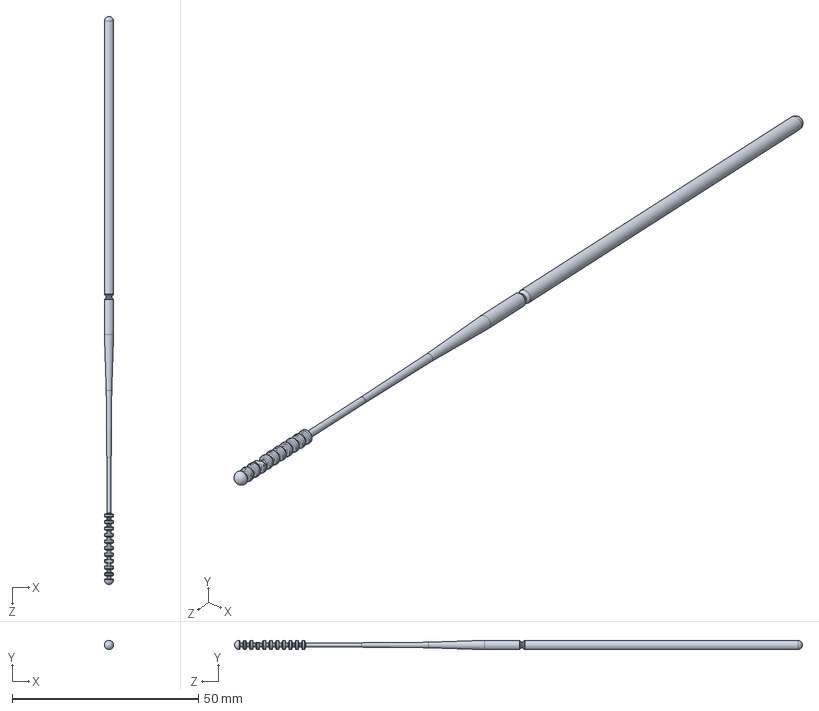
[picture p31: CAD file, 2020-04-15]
BIDMC/img/Wyss/Wyss_Swab_Release.SLDPRT
2.50 x 2.50 x 152.3 mm

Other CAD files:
BIDMC/img/Wyss/Wyss_Swab_Release.STL

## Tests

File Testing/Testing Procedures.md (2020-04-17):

These tests are designed to mitigate harm and ensure patient safety during operation.
These are suggestions and a work in progress and require further specification... please suggest/edit/add/comment, etc...

NOTE:

1. These tests should be performed on swabs that have *already undergone sterilization*.
The sterilizaiton process (e.g. autoclave) may affect material properties of the swabs.

2. These tests should be performed at various temperatures (freezing and room temperatures).
Drive-through clinics can have the swabs sitting in freezing conditions.
Indoor hospital can have the swabs at room temperature.

# Mechanical Testing Procedures
1) static load breaking test (represents bending the swab - shouldn't shatter, and should break at break-point)
   - fix proximal end of swab (hand side)
   - apply static load to distal end (absorbent side)
   - measure angle and load at which breaking occurs
   - note location of where breaking occurs (e.g. at snap-point or on neck or bulb)
   
2) axial load deformation/breaking test (represents pushing against an obstruction)
   - fix distal end of swab (absorbent side)
   - starting from 0, increase axial load to proximal end of swab (hand side)
   - measure load at which swab plastically deforms or breaks
   - measure where breaking occurs (e.g. at snap-point or on neck or bulb)

3) dynamic load breaking test (represents patient recoil of head)
   - fix proximal end of swab (hand side)
   - apply static load to distal end (absorbent side)
   - measure breaking with load
   - measure where breaking occurs (e.g. at snap-point or on neck or bulb)
   
4) bending plastic deformation test (represents any curvature the swab faces in nasopharynx)
   - fix proximal end of swab (hand side)
   - apply static load to distal end (absorbent side)
   - release load and allow swab to "relax"
   - measure deformation angle of "relaxed" swab with load
   - ensure swab bends and flexes less than maximum angle and more than maximum angle
   TODO: *specify maximum angle-per-load constraints*

5) elasticity test - spring-back (represents slight bump that swab has to go over when inserted)
   - fix proximal end of swab (hand side)
   - apply static load to distal end (absorbent side)
   - release load and allow swab to relax
   - measure deformation angle of swab
   - measure bending angle with load
   - ensure swab bends and flexes less than maximum angle and more than maximum angle

6) rotational test - turn until failure (this is to simulate the tip getting stuck/caught while the swab is being rotated in the nasopharynx) 
   - fix distal end of swab (absorbent side)
   - apply rotation (torque) to proximal end (hand side)
   - measure torque-theta profile
   - measure number of rotations until failure/breakage
   - measure point of failure 
   - note maximum torque until plastic deformation
   
7) rotation test in curved tube (to simulate turning of the swab in the nasopharynx after being bent)
   - use a bent piece of tubing (like surgical tubing, but fixed in shape (3d print one?)
   - insert distal end of swab into tube up to breakpoint
   - apply rotation (torque) to proximal end of (hand side)
   - measure torque-theat profile over the course of multiple turns
   - note maximum torque

8) tip abrasion 
   - measure dry weight of swab
   - place distal end of swab (absorbent end) next to simulated tissue (todo: spec pressure and material (e.g. moist chicken?)
   - apply rotation to proximal end (hand side) at hand twirling speed (60 RPM?) for 10 seconds
   - remove swab and wash and dry
   - measure new dry weiht of swab
   - note difference in swab weights (to measure wheter / how much tip has abraided)
   
9) tip crushing 

10) cycle loading

# Absorption Testing Procedures
Use food coloring and viscous solution (match nasopharyngeal fluid viscosity => glycerine / honey? TODO: find good mix)

1) absorption test (to test how much fluid is absorbed by swab)
   - measure swab dry weight using a microgram scale (tare with a plate)
   - fill a glass/vial/beaker with fluid (ideally match nasopharyngeal fluid viscosity > water)
   - dip swab until tip into container
   - pull swab out
   - measure swab wet weight using a microgram scale
   - record difference in swab weights
   
2) absorption & release tests (to test how much fluid is absorbed and then released by the swab into reaction chamber)
   - measure dry weight
   - measure 
   
OTHER METHODS   
   TODO: *quantify absorption of current swabs and test against current/old standard*
   method #1 with water, narrowest graduated cylinder you can find or tape a ruler/measuring tape to a test tube
   - fill tube with a known volume of water, note initial volume from bottom of the meniscus
   - slowly submerge the entire tip (all of the swabbing features) into the water, keep submerged for 5s, slowly withdraw
   - repeat for total of 10 swabs
   - measure the change in height of the water level, calculate total volume absorbed and average volume absorbed by each swab
   
   method #2 with water, wax paper/parafilm, microbalance (biology or chemistry labs should have one, some mechanical labs) [video](https://drive.google.com/file/d/1JOp8rVTZRIyFNDBDuPVH94QhuYIPi7Vu/view)
   - crease the wax paper so water will sit in the middle
   - place the paper on the microbalance and add ~1ml of water. Tare the balance
   - Hold the swab horizontally above the water droplet.  Slowly lower the swab into the droplet of water and rotate 180 degrees in both directions, ensuring the swab is completely submerged into the droplet and stays submerged for 2 seconds then slowly raise the swab to remove it from the water
   - repeat for a total of 10 swabs
   - record the amount of water removed from the scale and calculate the amount abosorbed by each swab.
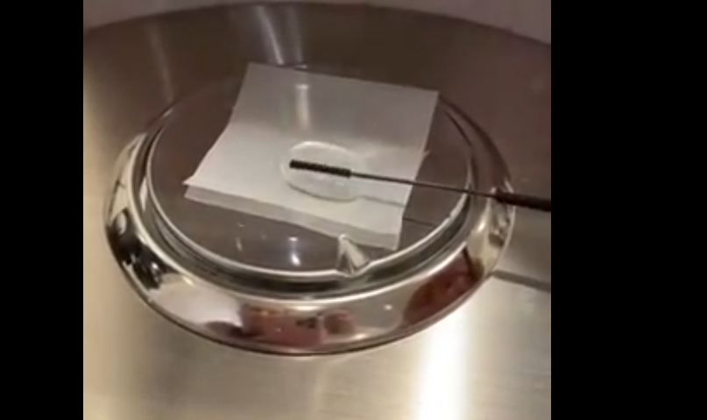
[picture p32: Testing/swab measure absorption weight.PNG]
   

# Biological/Chemical Testing Procedures
1) test that swab absorbs viral RNA particles
2) test that swab does not interfere with PCA/reagents
   
# Sample Collection Testing Procedures
1) with Methylene blue stain solution
   - do cheek swab (try to air out mouth and pick a less saliva-coated part of the cheek) or NP swab
   - smear onto a glass slide
   *if the smear doesn't result in any visible material left on the slide, place 50ul of buffer solution (saline, PBS, EPA water, etc) on the slide and roll the swab around in the buffer, dragging the liquid around the slide surface. [Video here](https://www.dropbox.com/s/coizu1qvzxpvwau/cheek%20swab%26stain%20w%20methylene%20blue%20for%20spiky%20swabs%20using%2050ul%20buffer%20to%20wet%20swab.mp4?dl=0)
   - add 2 drops (~80ul) of methylene blue solution to the slide
   - cover with a cover slip and image
   - epithelial cells and bacteria should be visible under 4-10x magnification
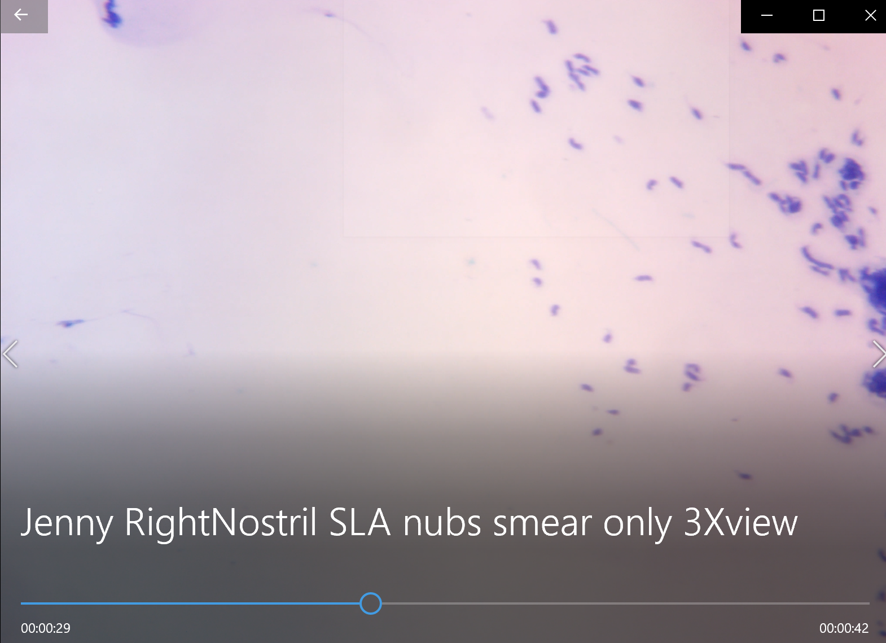
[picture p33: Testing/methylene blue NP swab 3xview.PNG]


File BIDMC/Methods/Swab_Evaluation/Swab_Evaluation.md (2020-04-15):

## Methods:

### Physical evaluation:

Test swabs were examined by two infectious disease physicians. Samples were compared against standard clinical use nasal pharyngeal  swabs [Copan] and evaluated for the degree of overall stiffness/elasticity, tip head diameter, and break off points. Specific evaluations are as follows in no particular order.

1: The tip head was evaluated on whether it could easily and repeatedly be folded back upon itself and return to the normal axis of the swab.

2: The degree of flexibility  as well as the diameter of the tip head was evaluated based on the presumed difficulty of inserting it into the posterior nasopharynx.

3: The swab neck was evaluated based on the degree of flexibility and on the presumed efficacy of insertion into the posterior nasopharynx.

4: Placement and efficacy of break points for placement into vial. Upon consultation, swabs were scored on a pass-fail system based on their over performance.
Test swabs were scored on a pass-fail system, with comments recorded <a href="/BIDMC/np_swab_results.xlsx">here</a>.

### Gram Stain:
Prototypes were used for a cheek swab and subsequently smeared onto microscopy slides. Slides were then treated according to the BD BBL gram stain test kit protocol and examined at 10x-40x magnification in comparison to Copan swabs. Qualitatively, prototype swabs were passed if slides had a non-negligible, as compared to negative controls, quantity of bacteria. [1]

The specifics of this protocol are as follows:

Cheek swabs were performed before the swab tips were applied to microscopy plates, producing a smear. Smears were then flooded with Gram Crystal Violet for 1 minute and subsequently rinsed with cold water. Next, slides were flooded with Gram Iodine or Stabilized Gram Iodine for 1 minute before rinsing with cold water.  Color was next removed from slides with Gram Decolorizer for up to a minute before again rinsing slides with cold water. Counterstain (Gram Safranin or Gram Basic Fuchsin)  was then flooded onto slides for up to one minute and then rinsed with cold water. After air drying, slides were examined at 10x-40x magnification.

### PCR testing:
Unused test swabs were placed in 3mL aliquots of modified CDC viral transport media composed 500mL Hank's balanced salt solution, 10mL of heat inactivated FBS, 100μg/mL Gentamycin, 0.5μg/mL Fungizone, and 10mg/L Phenol red [2]. Samples next underwent SARS-CoV-2  real-time reverse transcriptase polymerase chain reaction (rRT-PCR) on an Abbott M2000 automated platform [3].  Materials that affected the negative and positive controls of the of the rRT-PCR reactions, specifically altering the binding of internal control primers, were failed and vice versa.

The procedure is briefly described as follows.

0.5 mL samples are automatically using Abbott mSample Preparation SystemDNA, which relies on magnetic microparticle-based reagents to dissociate and capture Sars-Cov-2  virions before loading onto a 96 deep well plate.  Samples are then spiked with an unassociated RNA spike, which serves as an internal, positive control (IC). A master mix of SARS-CoV-2 Oligonucleoide Reagent, Thermostable rTth Polymerase Enzyme, activation reagent, and samples are added to the 96 well plate before amplification.

Target RNA is converted to cDNA by reverse transcriptase prior to SARS-CoV-2 and IC primers anneal and are elongated. Thermal cycling then allows for dissociation of the cDNA:RNA  bond at high temperatures  before RNA primers bind the cDNA and are elongated at lower temperatures. In total, SARS-CoV-2 RdRp, SARS-CoV-2 N, and IC are amplified.

Abbott m2000rt read cycles are based on real-time fluorescence detection of annealed primers at low temperatures. Specifically, SARS-CoV-2 primers have fluorescent moiety covalently bound to the 5' end, and a quencher moiety attached end, allowing for fluorescent detection only when the probe is bound to the target. The IC probe has a similar design, but with a different fluorophore.

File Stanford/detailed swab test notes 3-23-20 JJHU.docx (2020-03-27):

Today’s testing focused on the Abiogenix swab design with a nubbed tip (https://github.com/HMS-RIC/Covid19-NP-Swab/tree/master/design_files/abiogenix_swab_nubs), modified and printed in PA11 by HP, and also standardizing test methods (updated in https://github.com/HMS-RIC/Covid19-NP-Swab/blob/master/Testing/Testing%20Procedures.md).

For comparison I also used the same design printed in a proprietary epoxy on an SLA printer (this is not one of the official materials under consideration), and a Copan NP swab. Swabs were done by a doctor who has been doing shifts at a drive-through test site and grabbed a couple extra swabs on her way over.

Test 1, clinical evaluation:

- The SLA part is the stiffest, followed by Copan, then PA11. All were flexible but strong enough to maneuver through narrow passages (push through a lightly closed fist) and none felt too fragile. The tip was rough when jabbed into the back of the hand but not painful.
- The flocking was nice and soft on fingertips and was nicer in the lower nostril but I couldn’t tell a difference higher up.
- Doing the NP swabs on the doctor (person A) and me, both of us had one fairly blocked nostril and one clear one. There didn’t seem to be much of a difference in being able to get to the NP between the different swabs. For me all three caused a burning/stinging sensation once they were past the nasal cavity but none felt worse than the others. The general sensation and overall experience was unpleasant enough that I didn’t notice any difference between the Copan flocked tip and the others. Person A didn’t get a Copan swab but said both printed parts were acceptable to use and to have the test done.
- Snapping off – she’s been actually putting the VTM vial in a holder in front of her and grabbing the swabs with both hands on either side of the break point to snap it in two. That was easy for both printed parts. I snapped them off against a 15ml falcon tube, worked perfectly on the first try for both parts.

Test 2, sample collection

- All swabs came out wetted, most with some visible mucus between the rows of nubs. Rotating against the NP seems to have ‘spooled’ strands of mucus around the swab, captured between nubs (couldn’t get an in-focus picture of this). Swiping the 3D printed designs against a slide didn’t visibly leave much behind, sometimes just an array of dots as the nubs contacted while rolling the swab tip against the slide. The 3D printed swab smears only covered ~5-20% of the slide area covered by a smear from a cotton swab or the Copan swab (almost continuous coverage)
- To try and pull more material off the swab for staining we tried putting a drop of buffer (used EPA water but saline or PBS would work) then rolling the swab back and forth through the liquid.
- Results!
  - Don’t have a great way to count cells and field of view isn’t big enough to get a great idea of density so at the end are links to videos of panning over the various slides, all at the same magnification. Note I’m currently getting over a sinus infection and my samples are completely full of grossness even though I wasn’t that mucus-y. Conclusions below if you don’t have time to watch the videos.
  - More material was visibly transferred to the slide from the direct (no extra buffer) smear, probably because the mucus stuck directly to the dry slide but not as well to a wet slide. Staining showed plenty of bacteria in the mucus steaks for both methods, but loose cells/bacteria were much more common in the samples smeared with buffer.

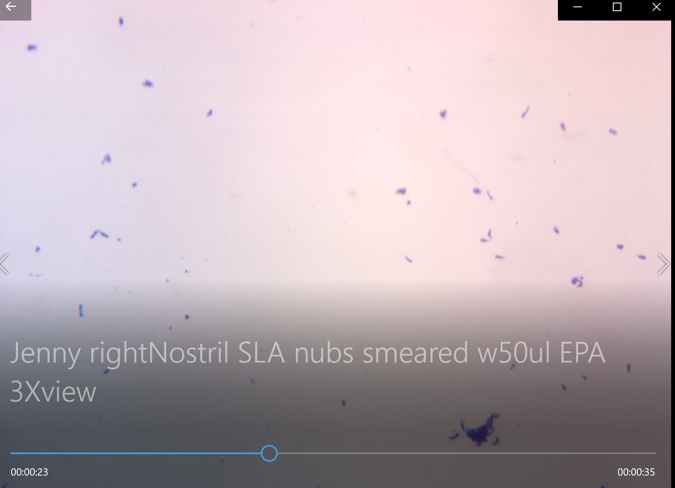
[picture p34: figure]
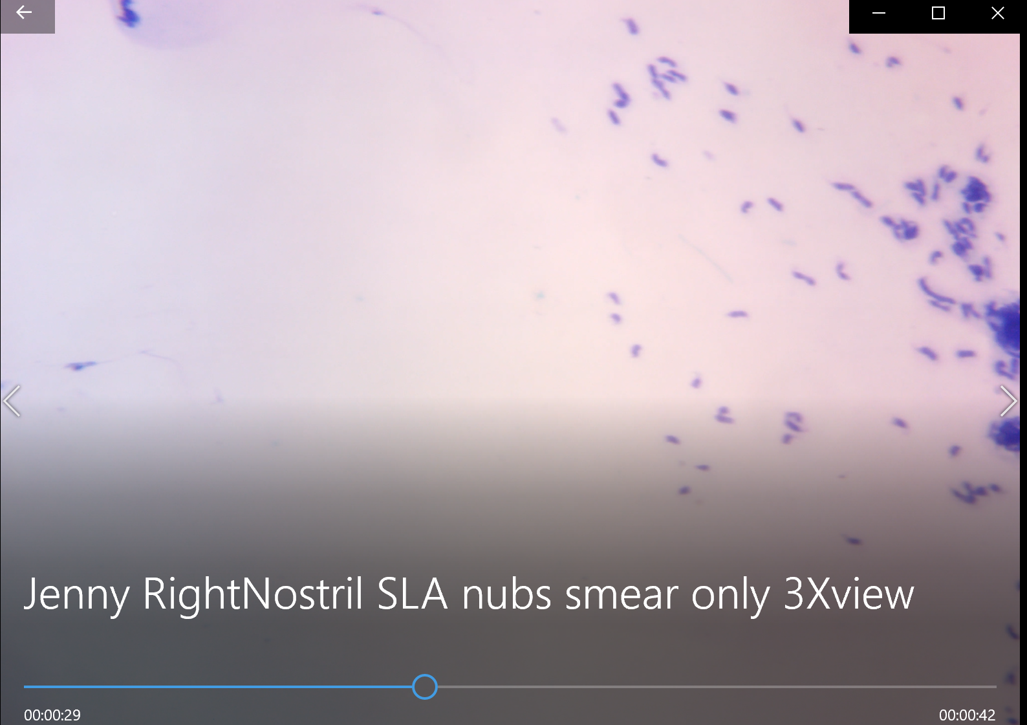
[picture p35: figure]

- My conclusions:
  - if the swab comes out coated with a visible amount of wet sample either filling/inside the swab or sitting on the swab (not fully absorbed inside), it has cells/bacteria inside that fluid and has probably picked up enough sample to be useable for PCR. See https://www.dropbox.com/s/wlb316jv5kuow6q/IMG_20200323_193553%5B1%5D.jpg?dl=0 , if you zoom in you can see mucus between the nubs and fluid filling in the rest of the volume of the tip.
  - If the swab has enough fluid/mucus sticking out from the tip to leave a smear on the slide, that will give a representative idea of what cells/bacteria are being picked up. If the swab looks “dry” or after attempting to smear no material is visibly left on the slide then I would recommend rolling it in a drop (50ul worked well for the methylene blue assay, gram stain may be different) of fluid on the slide to help wash material off of the swab to make sure material isn’t just ‘trapped’ inside the swab geometry in a way that could elute but won’t smear well. Video of this method here: https://www.dropbox.com/s/coizu1qvzxpvwau/cheek%20swab%26stain%20w%20methylene%20blue%20for%20spiky%20swabs%20using%2050ul%20buffer%20to%20wet%20swab.mp4?dl=0
  - The 3D printed swabs are definitely yielding less than the Coban swab, but with the quick staining method we really can’t tell how much of that is due to sample collection vs sample transfer to the slide. I’ll follow up with Dr. Ray Monnet at UW who suggested doing a study of sample collection efficiency (using a controlled viral stock solution) from our various swabs vs commercial but don’t think that should block us from moving forward for now – it would just be a useful data point on the expected relative sensitivity of the 3d printed vs manufactured swabs when viral counts are low.
  - Updated the testing page (https://github.com/HMS-RIC/Covid19-NP-Swab/blob/master/Testing/Testing%20Procedures.md) with a method to compare the absorbancy of different swabs with fairly available tools, but the swab+stain test sems the most relevant, so maybe it’s worth just finding nearby microbiology labs who can help with that work. I mixed up the methylene blue in ~15 minutes and each sample takes 5-10 minutes to swab, stain, image.

Test 3: PCR

- Gave samples of the HP PA11 material to UW virology for testing. A friend will autoclave more PA11 samples tomorrow and if both those tests pass we’ll also PCR the autoclaved samples to make sure the high temps don’t damage the plastic in a way that affects the reaction. Should also have PA12 samples in hand for PCR test tomorrow.

My overall conclusions from tests 1-2. I think we can make a completely (non-flocked) 3D printed part that is clinician/patient acceptable and while less effective than the Coban swab, in most cases collects enough sample for a positive ID. From my sample size of 2 (my friend and the medical assistant who swabbed me for my real test last week) the people who are going to be doing high throughput swabbing don’t have a ton of training on this and aren’t going to be too picky, and from their point of view patients are super grateful to be getting the test and can tolerate the brief discomfort/even slight pain. So we should put effort towards not making this a torture device but don’t need to optimize too much here for the first short term “fill the immediate gap” run.

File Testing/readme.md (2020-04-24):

Lawrence Livermore National Laboratory has graciously offered to test swabs for mechanical and absorption testing.

Please contact Angela Tooker at tooker1@llnl.gov

There are suggested mechanical and absorption testing files in this folder as well.

Anecdotally, the recommended max-torque at which point a clinicial would stop rotating a swab was estimated to be 3lbf-in, and the max pull-out force (e.g. for tensile tests) was estimated as between 1 and 5lbs.

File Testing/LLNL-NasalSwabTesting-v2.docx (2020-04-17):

LAWRENCE LIVERMORE NATIONAL LABORATORY

NP Swab Testing

Top Priority Tests

1. Pull (Tensile/Elongation) Test
  a. Goal: Mimic pulling the NP Swab out of the NP space.
  b. Test: Secure both ends of the NP Swab and apply a tensile force until the swab breaks.
    i. Record: Load, Extension, Location of the Break Point on the Swab
  c. LLNL Status: Ready for testing
2. Rotational Test
  a. Goal: Mimic rotating the NP Swab in the NP space for sample collection.
  b. Test: Secure both ends of the NP swab and apply a rotational force at the handle until the swab breaks.
    i. Record: Torque, # of Rotations, Location of the Break Point on the Swab
  c. LLNL Status: Confirming necessary hardware is onsite for this test.

Additional Tests (Need To Be Put in Priority Order)

- Crush/Compression Test
  - Goal: Mimic the NP Swab head getting pushed and squeeze into the NP space.
  - Test #1: Lay the NP Swab head between 2 flat plates and apply a compression force until the NP Swab head is compressed to half it’s original width.
    - Record: Load, Extension
    - Record the weight of the swab pre/post testing to evaluate whether material is lost due to crushing.
  - Test #2: Hold the NP Swab just below the head and apply a compression force (axially) until the NP Swab head is compressed to half it’s original height.
    - Record: Load, Extension
    - Record the weight of the swab pre/post testing to evaluate whether material is lost due to crushing.
  - LLNL Status: Ready for testing
- Push (Compression) Test
  - Goal: Mimic pushing the NP Swab into the NP space.
  - Test: Secure both ends of the NP Swab and apply a tensile force until the swab breaks.
    - Record: Load, Extension, Location of the Break Point on the Swab
  - LLNL Status: Ready for testing
- Break Test
  - Goal: Mimic the breaking of the NP Swab in the Vial.
  - Test: Standard 3-point bend test to measure the load required to break the swab at the break point.
    - Record: Load, Extension
  - LLNL Status: Ready for testing
- Insertion Test
  - Goal: Mimic pushing the NP Swab into the NP space.
  - Test: Secure one end of the NP swab and push the other into the simulated NP Space.
    - Record, Load?, Extension?
  - LLNL Status: Have ordered an NP Space model to evaluate ease of insertion of the NP Swab into the NP Space – needs evaluation prior to testing beginning. It might be possible to combine this with the Instron and measure the insertion forces.
- Abrasion Test
  - Goal: Mimic the NP Swab rubbing against the interior of the NP space.
  - Test #1: Place the NP Swab head between two flat plates (coated with a mucosal lining surrogate) and apply a small loading force. Pull the NP Swab straight out from between the two flat plates.
    - Visually evaluate the surface of the swab and the plates to determine if the NP Swab is leaving particulates behind or if an unacceptable amount of damage is happening to the mucosal lining surrogate.
  - Test #2: Place the NP Swab head between two flat plates (coated with a mucosal lining surrogate) and apply a small loading force. While rotating the NP Swab, pull it out from between the two flat plates.
    - Visually evaluate the surface of the swab and the plates to determine if the NP Swab is leaving particulates behind or if an unacceptable amount of damage is happening to the mucosal lining surrogate.
  - LLNL Status: Have ordered mucosal lining surrogate – needs evaluation prior to testing beginning.
- Flexural/Fatigue Test
  - Goal: Mimic the flexibility of the NP Swab (and the bending forces it will see).
  - Test #1: Secure handle of the NP Swab and bend the head of the NP Swab downward (or upward) a fixed distance.
    - Record: Load, Extension
  - Test #2: Secure the handle of the NP Swab and bend the head of the NP Swab downward (or upward) a fixed distance. Release the NP Swab to it’s neutral position and repeat the bending.
    - Record: Load, Extension
  - LLNL Status: Confirming necessary hardware is onsite for this test
- Absorption/Release Test (Non-Biological)
  - Goal: Determine the fluid uptake and release properties of the NP Swab.
  - Absorption Test: Submerge the NP Swab in the surrogate material.
    - Record: Weight of the NP Swab before and after submersion.
  - Release Test: Submerge the NP Swab in the release material.
    - Record: Weight of the NP Swab before and after submersion, Measure the amount of fluid released using the spectrophotometer
  - LLNL Status: All hardware is onsite and ready for use. Appropriate material surrogates need to be determined.

Author: Angela TookerPage 1 of 2

LLNL Swab Testing Procedures v2.004/03/2020

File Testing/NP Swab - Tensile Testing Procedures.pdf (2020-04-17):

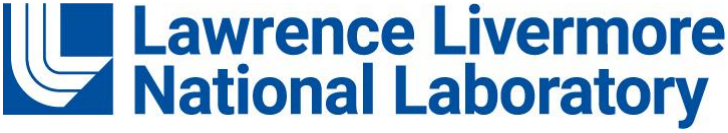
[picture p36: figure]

# Swab Tensile Testing Procedures

Contact:
Chris Spadaccini (spadaccini2@llnl.gov) Eric Duoss (duoss1@llnl.gov)
Maxim Shusteff (shusteff1@llnl.gov) Angela Tooker (tooker1@llnl.gov) Razi Haque (haque3@llnl.gov)

Report Prepared By:
Angela Tooker

This document was prepared as an account of work sponsored by an agency of the United States government. Neither the United States government nor Lawrence Livermore National Security, LLC, nor any of their employees makes any warranty, expressed or implied, or assumes any legal liability or responsibility for the accuracy, completeness, or usefulness of any information, apparatus, product, or process disclosed, or represents that its use would not infringe privately owned rights. Reference herein to any specific commercial product, process, or service by trade name, trademark, manufacturer, or otherwise does not necessarily constitute or imply its endorsement, recommendation, or favoring by the United States government or Lawrence Livermore National Security, LLC. The views and opinions of authors expressed herein do not necessarily state or reflect those of the United States government or Lawrence Livermore National Security, LLC, and shall not be used for advertising or product endorsement purposes.

This work was performed under the auspices of the U.S. Department of Energy by Lawrence Livermore National Laboratory under Contract DE-AC52-07NA27344.
LLNL-TR-808538

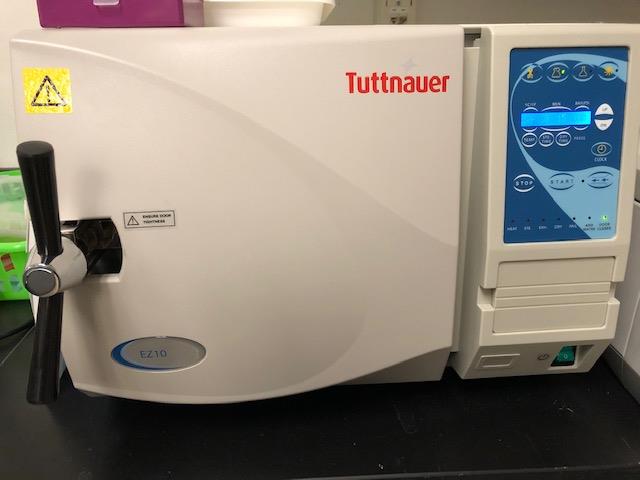
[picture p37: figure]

04/11/2020 | Page 2 of 10

Tensile Testing Procedure

1. Pre-Treatment – Autoclave
a. Note: Pre-treatment was performed on only a subset of the swabs tested.
b. Equipment
i. Tuttnauer EZ10 Automatic Autoclave (Figure 1)

Figure 1. Autoclave used for pre-treatment of swabs.

c. Materials
i. VWR Cat. NO. 89140-800 Self Sealing Sterilization Pouch (5.25in x 10in) (Figure 2)
d. Procedure
i. Swabs were placed inside the sterilization pouch. 10 swabs were placed in a single pouch (Figure 2).

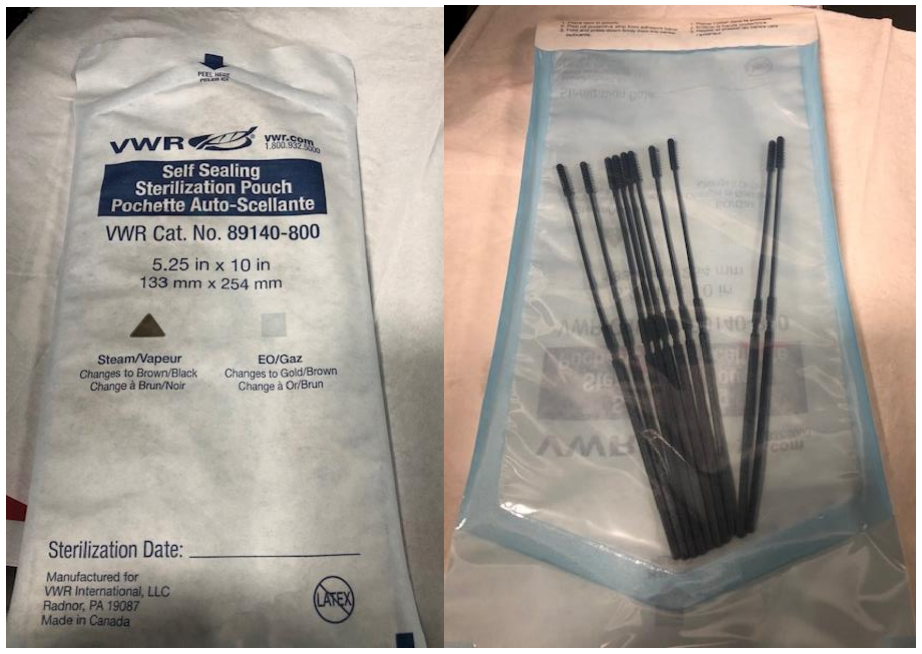
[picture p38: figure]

Figure 2. Swabs were placed inside a self-sealing sterilization pouch.

ii. Pouches were then placed inside the autoclave. Up to 4 pouches of swabs were autoclaved simultaneously.
iii. Swabs were autoclaved with the following settings:
1. Temperature: 250°F
2. Sterilization Time: 30 minutes
3. Dry Time: 15 minutes
4. (Note: The pressure during sterilization was 17psi.)
2. Tensile Testing
a. Equipment
i. Instron Model 5966 (Figure 3) running Bluehill Universal Software ii. 1kN Load Cell (Instron Model 2580-1KN) (Figure 3)
iii. Pneumatic Grips (Instron Model 2712-019) with serrated plates (0.5in height), controlled with 60psi of pressure (Figure 3)

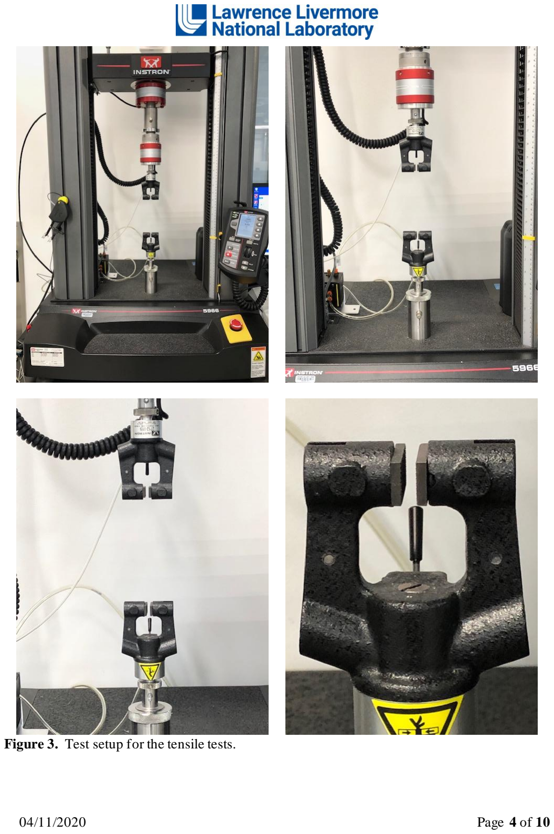
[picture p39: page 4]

Figure 3. Test setup for the tensile tests.

b. Procedure
i. Place the handle of the swab in the upper grips and close. The swab should not protrude above the height of the plates (Figure 4).

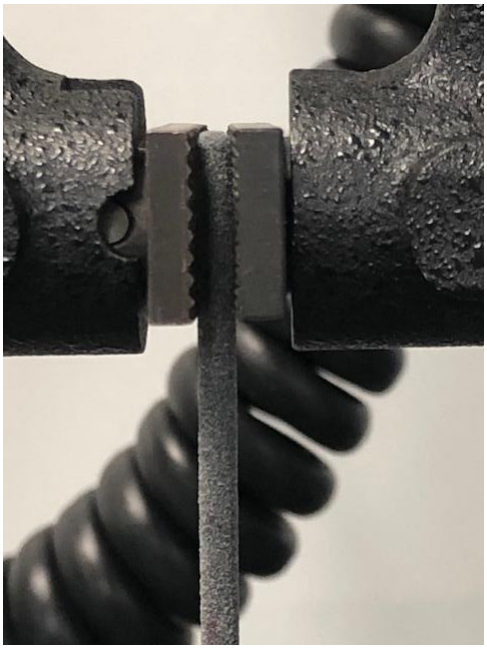
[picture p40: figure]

Figure 4. Image of the swab position inside the upper grips. The tip of the swab handle should be flush with the top of the grips.

ii. Secure the tip of the swab in the lower grips and close. The tip of the swab will protrude slightly below the height of the plates. The swab head should be at the top of the plates (Figure 5).

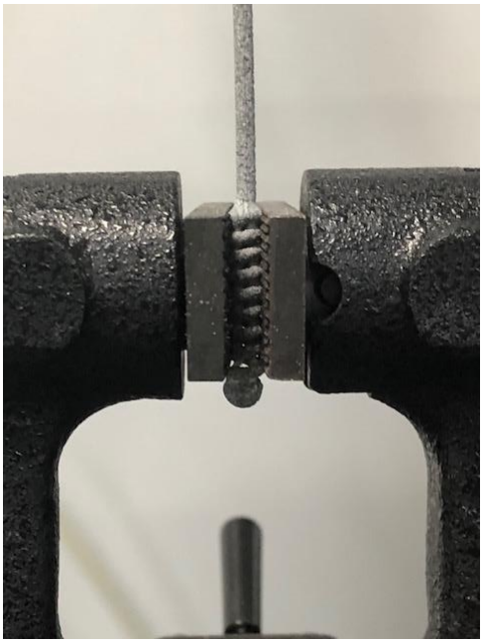
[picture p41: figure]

Figure 5. Image of the swab inside the lower grips. The top of the swab head should be flush with the top of the grips. The tip of the swab head will protrude below the grips.

iii. Adjust the height of the upper grip to remove any slack (Figure 6). Make sure not to pre-load the swab.


Figure 6. Image of the swab positioned in the grips. Prior to testing, any slack in the specimen should be removed by adjusting the height of the upper grips. Ensure that this slack-removal process does not pre-load the swab.

iv. Balance both the force and displacement.
v. Start the tensile test procedure:
1. Rate of Test: 25mm/min
2. Test End: 40% change in Force
vi. The data is automatically collected for Time, Force, and Displacement. The test should automatically conclude when a 40% change in Force is detected (i.e. when the swab breaks). This data point is recorded as the “Break Point.”
vii. The physical location of the break point was classified as:
1. “Neck” (for swabs breaking in the neck region – Figure 7),
2. “Head-Neck” (for swabs breaking at the joint between the head and the neck – Figure 8),
3. “Head” (for swabs breaking in the head region – Figure 9), or
4. “Breakpoint” (for swabs that broke at the desired breakpoint on the handle – Figure 10).


Figure 7. Representative images of the swabs classified as breaking at the “Neck.”

Figure 8. Representative image of a swab classified as breaking at the “Head-Neck.”


Figure 9. Representative image of a swab classified as breaking at the “Head.” The break location is shown circled in red in the bottom image. In many cases, though, the actual break location was not visually observable and the swabs were classified as having broken based on the force-elongation data.


Figure 10. Representative image of a swab classified as breaking at the “Breakpoint.”

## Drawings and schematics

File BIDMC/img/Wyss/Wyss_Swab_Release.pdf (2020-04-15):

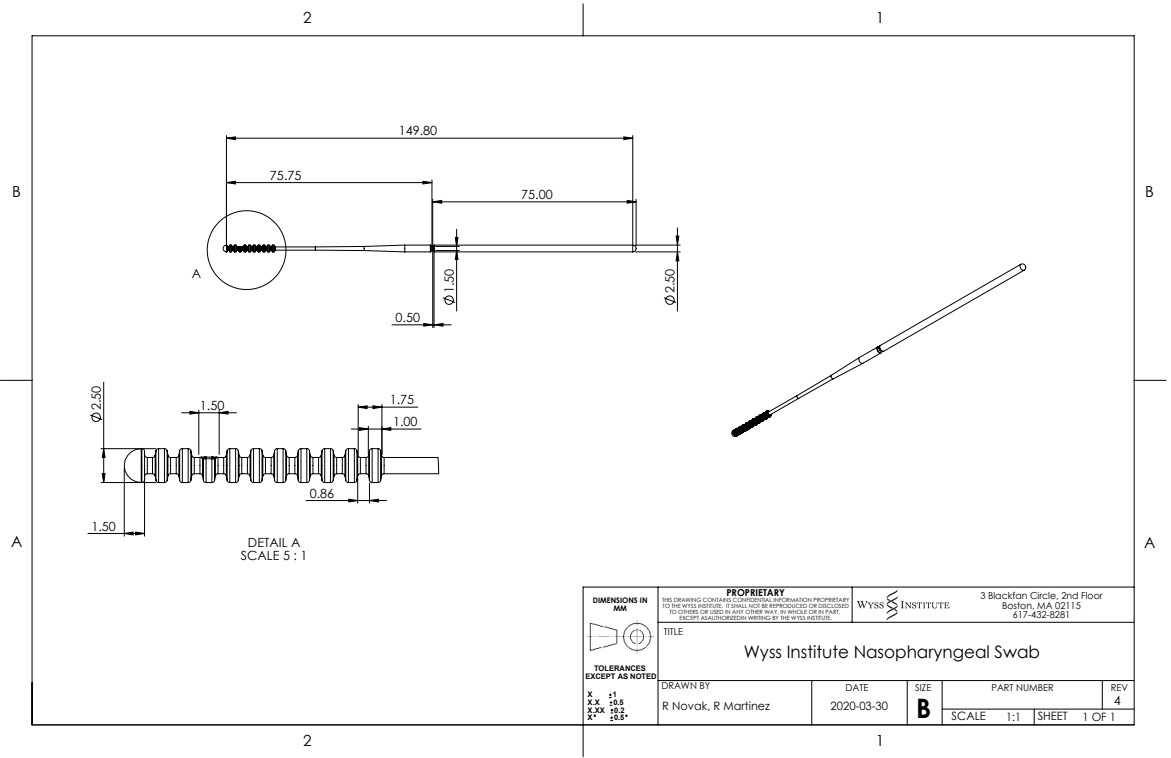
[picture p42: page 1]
DIMENSIONS IN; EXCEPT AS NOTED; DETAIL A SCALE 5 : 1

3 Blackfan Circle, 2nd Floor
Boston, MA 02115

THIS DRAWING CONTAINS CONFIDENTIAL INFORMATION PROPRIETARY
TO THE WYSS INSTITUTE. IT SHALL NOT BE REPRODUCED OR DISCLOSED
TO OTHERS OR USED IN ANY OTHER WAY, IN WHOLE OR IN PART,
EXCEPT ASAUTHORIZEDIN WRITING BY THE WYSS INSTITUTE.
TITLE

Wyss Institute Nasopharyngeal Swab

DRAWN BY R Novak, R Martinez | DATE 2020-03-30 | SIZE B 4 | PART NUMBER | REV

SCALE 1:1 | SHEET 1 OF 1

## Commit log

2020-03-30 updating results
    [np_swab_results.xlsx, np_swab_results_03_30_2020.xlsx]
2020-03-31 Updating results 2020_03_31
    [np_swab_results.xlsx, np_swab_results_03_31_2020.xlsx]
2020-04-01 Added images
    [np_swab_results.xlsx]
2020-04-02 results updated 2020-04-02
    [np_swab_results.xlsx, np_swab_results_04_02_2020.xlsx]
2020-04-03 USF STL pointer
    [USF Roundnose 70 mm breakpoint v1.stl]
2020-04-05 added Wyss injection molded design files
    [Wyss_Swab_Release.SLDPRT, Wyss_Swab_Release.STL]
2020-04-10 Note to Injection Mold Manufacturers
2020-04-14 Results update
    [np_swab_results.xlsx, np_swab_results_04_13_2020.xlsx]
2020-04-17 updated results
    [np_swab_results.xlsx]
2020-04-22 results and pictures updated
    [np_swab_results.xlsx, np_swab_results_04_22_2020.xlsx]
2020-04-23 swab designs
    [np_swab_results_04_23_2020.xlsx]
2020-04-24 Added sample Participant Information Sheet
2020-05-07 create nasal_swab_results
    [nasal_swab_results.xlsx]
2020-05-12 updated np results
    [nasal_swab_results.xlsx, np_swab_results.xlsx, np_swab_results_05_11_2020.xlsx]
2020-06-11 Create nasal_swab_results_2020_06_11 .xlsx
    [nasal_swab_results_2020_06_11 .xlsx]
